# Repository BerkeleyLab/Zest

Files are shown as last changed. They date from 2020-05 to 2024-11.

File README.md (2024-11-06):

# Zest board

Zest (Z=e^(st)) is a double FMC mezzanine board performing Analog to Digital and Digital to Analog conversions.
This board is mainly used as a part of Radio Frequency (RF) controls electronics systems in particle accelerators.
Over 400 units have been manufactured by Berkeley Lab and SLAC National Laboratories and is the ADC/DAC board base design of the
LCLS-II (Linac Coherent Light Source II) Low-Level RF (LLRF) system at SLAC.

The schematic is in gschem format; to work with it you
need [gschem](http://wiki.geda-project.org/geda:gaf) installed.
Tested on [Debian](https://www.debian.org) Jessie, Stretch, or Buster, where
you simply `apt-get install geda-gschem`.

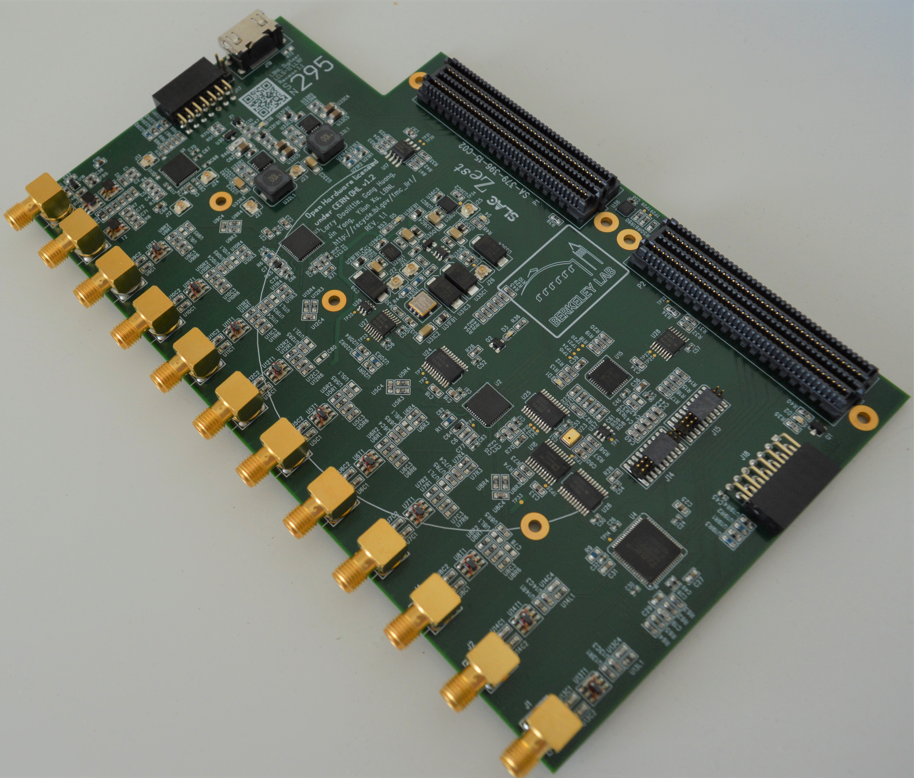
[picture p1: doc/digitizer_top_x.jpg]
Image of completed board
 

The Zest board features:

* 8 x transformer-coupled inputs sampled at 95 MS/s (2 x AD9653)
* 2 x transformer-coupled outputs sampled at 190 MS/s (AD9781)
* Input clock source up to 3 GHz (LMK01801, no on-board oscillator)
* Extra clock divider output
* 2 x Pmod digital I/O
* Interface to FPGA via dual-LPC-FMC connectors
* 181.8 x 110 mm, 8-layer, with notch to accommodate Xilinx FMC eval boards, also known to work with [Marble](https://github.com/BerkeleyLab/Marble) and [Marble-Mini](https://github.com/BerkeleyLab/Marble-Mini)
* 4W power dissipation

This design has been skillfully ported to [KiCad](https://www.kicad.org/) 8 by Gang Huang.
Go [here](https://gitlab.com/lbl-boards/zest) for that work, now labeled Zest v1.2.

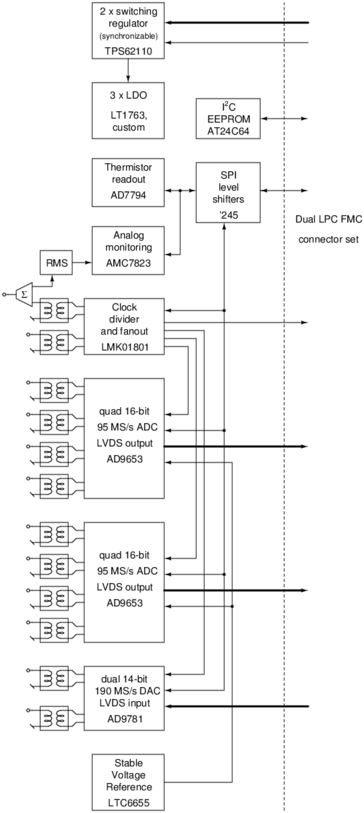
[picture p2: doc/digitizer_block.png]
block_diagram


## Schematics

To get PDF versions for reference:

  * Download the `djboxsym` tool. Put it in your PATH.

```bash
$ wget http://www.gedasymbols.org/user/dj_delorie/tools/djboxsym
$ echo "1a372fdef8e474119fae8acde38226f82271b62cd16b7f47b6b2408f0c0dd1ea  djboxsym" | sha256sum -c
djboxsym: OK
```

  * call `make` in `geda_library/symbol/djboxsym/`, which generates symbols from the included symbol templates
  * call `make` in `digitizer/`, which should generate `digitizer_schematic.pdf`

## Artwork/Gerbers

Created by Kathy Pham at SLAC using PADS.  The latest version is from May 19, 2017.
The PADS design imports the netlist exported from this gschem design.
These PADS pcb file is in the top directory in this repository (`PC-379-396-15-C02_DIGITIZER BOARD.pcb`) and the gerbers
are in the `gerbers` directory.

QR-code serial-number overlay Gerbers are generated with `qr_gen.py`.

## BOM

The BOM is also in the top directory in this repository (`PC-379-396-15-C02_DIGITIZER BOARD_XY.xlsx`).
This file was exported from the PADS design referenced above.

If you run `make merged_xy.csv`, you can merge the actual orderable part numbers (kept here
in the parts.data file) and get a usable xy assembly file for fabrication.

## Plastic Cover

One corner of the digitizer (by J3, clock input) has some fragile transformers
very close to where SMA wrenches are used.
It has proved helpful to have a protective cover in place to avoid damage.
This is designed in [OpenSCAD](http://www.openscad.org/) with a process that
matches up its features with the Gerber file; see covergen.py.
The OpenSCAD source file is cover1.scad.
OpenSCAD will export an STL file which is easily 3-D printed.

## References

 G. Huang, L. R. Doolittle, J. Yang, Y. Xu,
*"Low Noise Digitizer Design for LCLS-II LLRF,"* in NAPAC2016
[TUPOA40](https://accelconf.web.cern.ch/napac2016/papers/tupoa40.pdf).

## Copyright

Zest Copyright (c) 2019, The Regents of the University of California, through Lawrence Berkeley National Laboratory (subject to receipt of any required approvals from the U.S. Department of Energy), and The Board of Trustees of the Leland Stanford Junior University. All rights reserved.

This documentation describes Zest and is licensed under the CERN OHL v. 1.2.

NOTICE. This documentation was developed under funding from the U.S. Department of Energy and the U.S. Government consequently retains certain rights. As such, the U.S. Government has been granted for itself and others acting on its behalf a paid-up, nonexclusive, irrevocable, worldwide license in the documentation to reproduce, distribute copies to the public, prepare derivative works, and perform publicly and display publicly, and to permit others to do so.

You may redistribute and modify this documentation under the terms of the CERN OHL v.1.2. (http://ohwr.org/cernohl). THIS DOCUMENTATION IS PROVIDED BY THE COPYRIGHT HOLDERS AND CONTRIBUTORS "AS IS" AND ANY EXPRESS OR IMPLIED WARRANTIES, INCLUDING, BUT NOT LIMITED TO, THE IMPLIED WARRANTIES OF MERCHANTABILITY AND FITNESS FOR A PARTICULAR PURPOSE ARE DISCLAIMED. IN NO EVENT SHALL THE COPYRIGHT OWNER OR CONTRIBUTORS BE LIABLE FOR ANY DIRECT, INDIRECT, INCIDENTAL, SPECIAL, EXEMPLARY, OR CONSEQUENTIAL DAMAGES (INCLUDING, BUT NOT LIMITED TO, PROCUREMENT OF SUBSTITUTE GOODS OR SERVICES; LOSS OF USE, DATA, OR PROFITS; OR BUSINESS INTERRUPTION) HOWEVER CAUSED AND ON ANY THEORY OF LIABILITY, WHETHER IN CONTRACT, STRICT LIABILITY, OR TORT (INCLUDING NEGLIGENCE OR OTHERWISE) ARISING IN ANY WAY OUT OF THE USE OF THIS SOFTWARE, EVEN IF ADVISED OF THE POSSIBILITY OF SUCH DAMAGE. Please see the CERN OHL v.1.2 for applicable conditions.

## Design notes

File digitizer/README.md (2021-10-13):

# LCLS-II LLRF Digitizer Board

This directory holds the schematics and associated files (but not the layout)
for the LCLS-II LLRF Digitizer Board, currently Rev. 1.1.
It is in gschem format; to work with it you
need [gschem](http://wiki.geda-project.org/geda:gaf) installed.
Tested on [Debian](https://www.debian.org) Jessie or Stretch, where
you simply `apt-get install geda-gschem`.

Image of completed board [block diagram](../../doc/digitizer_block.png)

The digitizer board features:

* 8 x transformer-coupled inputs sampled at 95 MS/s (2 x AD9653)
* 2 x transformer-coupled outputs sampled at 190 MS/s (AD9781)
* Input clock source up to 3 GHz (LMK01801, no on-board oscillator)
* Extra clock divider output
* 2 x Pmod digital I/O
* Interface to FPGA via dual-LPC-FMC connectors
* 181.8 x 110 mm, with notch to accommodate Xilinx FMC eval boards
* 4W power dissipation

## Schematics

To get PDF versions for reference,
simply `make` in this directory.  The result is digitizer_schematics.pdf.

## Artwork/Gerbers

Created by Kathy Pham at SLAC using PADS.  Latest is 20170519.
The PADS design imports the netlist exported from this gschem design.
These PADS files are _not_ kept in this git repository, but
their SHA256 signatures are kept in the
[layout_20170519.sha256sum](layout_20170519.sha256sum) file in this directory.

QR-code serial-number overlay Gerbers are generated with `qr_gen.py`.

## BOM

Get a copy of the `PC-379-396-15-C02_DIGITIZER BOARD_XY.xlsx` file exported from
the PADS design reference above, and place it in this directory.

Then `make merged_xy.csv` to merge the actual orderable part numbers (kept here
in the parts.data file) and get a usable xy assembly file for fabrication.

## Plastic Cover

One corner of the digitizer (by J3, clock input) has some fragile transformers
very close to where SMA wrenches are used.
It has proved helpful to have a protective cover in place to avoid damage.
This is designed in [OpenSCAD](http://www.openscad.org/) with a process that
matches up its features with the Gerber file; see covergen.py.
The OpenSCAD source file is cover1.scad.
OpenSCAD will export an STL file which is easily 3-D printed.

## References

 G. Huang, L. R. Doolittle, J. Yang, Y. Xu,
*``Low Noise Digitizer Design for LCLS-II LLRF,''* in NAPAC2016
[TUPOA40](http://accelconf.web.cern.ch/AccelConf/napac2016/papers/tupoa40.pdf).

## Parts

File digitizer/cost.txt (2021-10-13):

As of 2015-08-21

Digi-Key BOM/shopping cart creation (based on orderable.txt) is
half-broken, but I can tell that qty. 25 parts cost is $743.42.

 2  ASP-134604-01   @newark          16.37
10  TCM4-19+        @minicircuits     2.09
 2  TCM2-43X+       @minicircuits     3.29
 1  TCP-2-33W+      @minicircuits     2.99

total non-Digi-Key: $63.21

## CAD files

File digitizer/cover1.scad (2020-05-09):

/* Digitizer cover to protect its transformers near J3 and J20 */
/* Obsolete, see cover2c.scad */
/* See also covergen.py */

/* 5 mm from board to attached SMA connector, which still fits in */
/* the 7.9 mm cutout for the board-mount SMA connector. */
/* 7 mm from board to the beginning of the hex section. */
/* Part is 5.5 mm thick, to avoid slight interference with SMA connectors found with a 6mm thick version. */

module cover()
{
  union() {
    difference() {
       union () {
          translate([0, -39.5, 2]) cube([40.5, 39.5, 3.5]);
          /* copper pad on board measures 5.8 mm dia */
          translate([37.55,-36.5, 0]) cylinder(r=2.9, h=4, $fn=30);
       }
       union () {
          /* 106.3 mil = 2.7 mm dia hole, tight clearance for 4-40 */
          translate([37.55, -36.5, -1]) cylinder(r=1.5, h=8, $fn=30);
          translate([ -1, -11.50, 0]) cube([10.6, 7.7, 8]);  /* J3  */
          translate([ -1, -26.75, 0]) cube([10.6, 7.7, 8]);  /* J20 */
          translate([ -1, -42.00, 0]) cube([10.6, 7.7, 8]);  /* J11 */
          /* TCM4-19 datasheet claims max height 4.06 mm, I measure 3.1 mm */
          translate([11.3, -15.2, 0]) cube([4.2, 4, 4.0]);  /* U34 */
          translate([17.3, -15.2, 0]) cube([4.2, 4, 4.0]);  /* T1 */
          translate([11.3, -26.0, 0]) cube([4.2, 4, 4.0]);  /* T1 */
          translate([39, -24, 1]) mirror(v=[1, 0, 0]) linear_extrude(height = 1.5) {
              text("LBNL", size = 6.2, font = "Liberation Sans");
          }
          translate([28, -34, 1]) mirror(v=[1, 0, 0]) linear_extrude(height = 1.5) {
              text("R3", size = 6.2, font = "Liberation Sans");
          }
       }
    }
    /* these are the stubs supposed to rest on the bare board */
    translate([0,    -3.6, 0]) cube([ 9.5, 3.6, 2]);
    translate([0,   -18.2, 0]) cube([ 9.5, 3.6, 2]);
    translate([0,   -33.1, 0]) cube([16.0, 5.2, 2]);
    translate([25.3, -6.1, 0]) cube([ 9.5, 6.1, 2]);
  }
}

cover();

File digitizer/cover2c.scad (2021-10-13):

/* Digitizer cover to protect its transformers near J3 and J20 */
/* See below for connection to covergen.py */

/* 5 mm from board to attached SMA connector, which still fits in */
/* the 7.9 mm cutout for the board-mount SMA connector. */
/* 7 mm from board to the beginning of the hex section. */
/* Part is 5.5 mm thick, to avoid slight interference with SMA connectors found with a 6mm thick version. */

module base_cube(x1, y1, dx, dy, h)
{
    translate([x1,  y1, 0]) cube([ dx, dy, h]);
}

/* Generated by covergen2.py */
include <cover2_layers.dat>

module cover()
{
  union() {
    difference() {
       union () {
          translate([0, -181.5, 2]) cube([40.5, 181.5, 3.5]);
          /* copper pad on board measures 5.8 mm dia */
          translate([37.55, -36.50, 0]) cylinder(r=2.9, h=4, $fn=30);
          translate([38.69, -77.90, 0]) cylinder(r=2.9, h=4, $fn=30);
          translate([32.47,-146.99, 0]) cylinder(r=2.9, h=4, $fn=30);
       }
       union () {
          /* 106.3 mil = 2.7 mm dia hole, tight clearance for 4-40 */
          translate([37.55, -36.50, -1]) cylinder(r=1.5, h=8, $fn=30);
          translate([38.69, -77.90, -1]) cylinder(r=1.5, h=8, $fn=30);
          translate([32.47,-146.99, -1]) cylinder(r=1.5, h=8, $fn=30);
          layer3();
          layer2();
          translate([39, -24, 1]) mirror(v=[1, 0, 0]) linear_extrude(height = 1.5) {
              text("LBNL", size = 6.2, font = "Liberation Sans");
          }
          translate([28, -34, 1]) mirror(v=[1, 0, 0]) linear_extrude(height = 1.5) {
              text("R4", size = 6.2, font = "Liberation Sans");
          }
       }
    }
    layer1();
  }
}

cover();

/* set up the initial view */
$vpr = [156, 0, 100];
$vpt = [56, -86, -71];
$vpd = 140;

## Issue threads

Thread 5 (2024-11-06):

### ISSUE TITLE
Paper link 404

### ISSUE THREAD

**Issue by mdavidsaver** [BerkeleyLab/Zest#5]
The CERN [link](http://accelconf.web.cern.ch/AccelConf/napac2016/papers/tupoa40.pdf) in the README now returns a 404.

https://github.com/BerkeleyLab/Zest/blob/43e8c67fba8082a3a21e5eda8ba646df3bf2c3b9/README.md?plain=1#L75C1-L77C80

**Comment by mdavidsaver** [comment]
I found what I think is a new URL.  Is this the same paper?

https://accelconf.web.cern.ch/napac2016/papers/tupoa40.pdf

**Comment by ldoolitt** [comment]
Yes.
`31e12ff99218b0af442ee49b99f9bdd18fad4b6ffb2036ee2ae2193ea4c42ac5  tupoa40.pdf`

**Comment by ldoolitt** [comment]
@mdavidsaver thanks for pointing this out!  Fixed.

**Comment by mdavidsaver** [comment]
You might want to add this citation to the README for the [gitlab](https://gitlab.com/lbl-boards/zest) project as well.

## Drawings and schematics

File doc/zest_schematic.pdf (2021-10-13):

# Clock distribution ADC

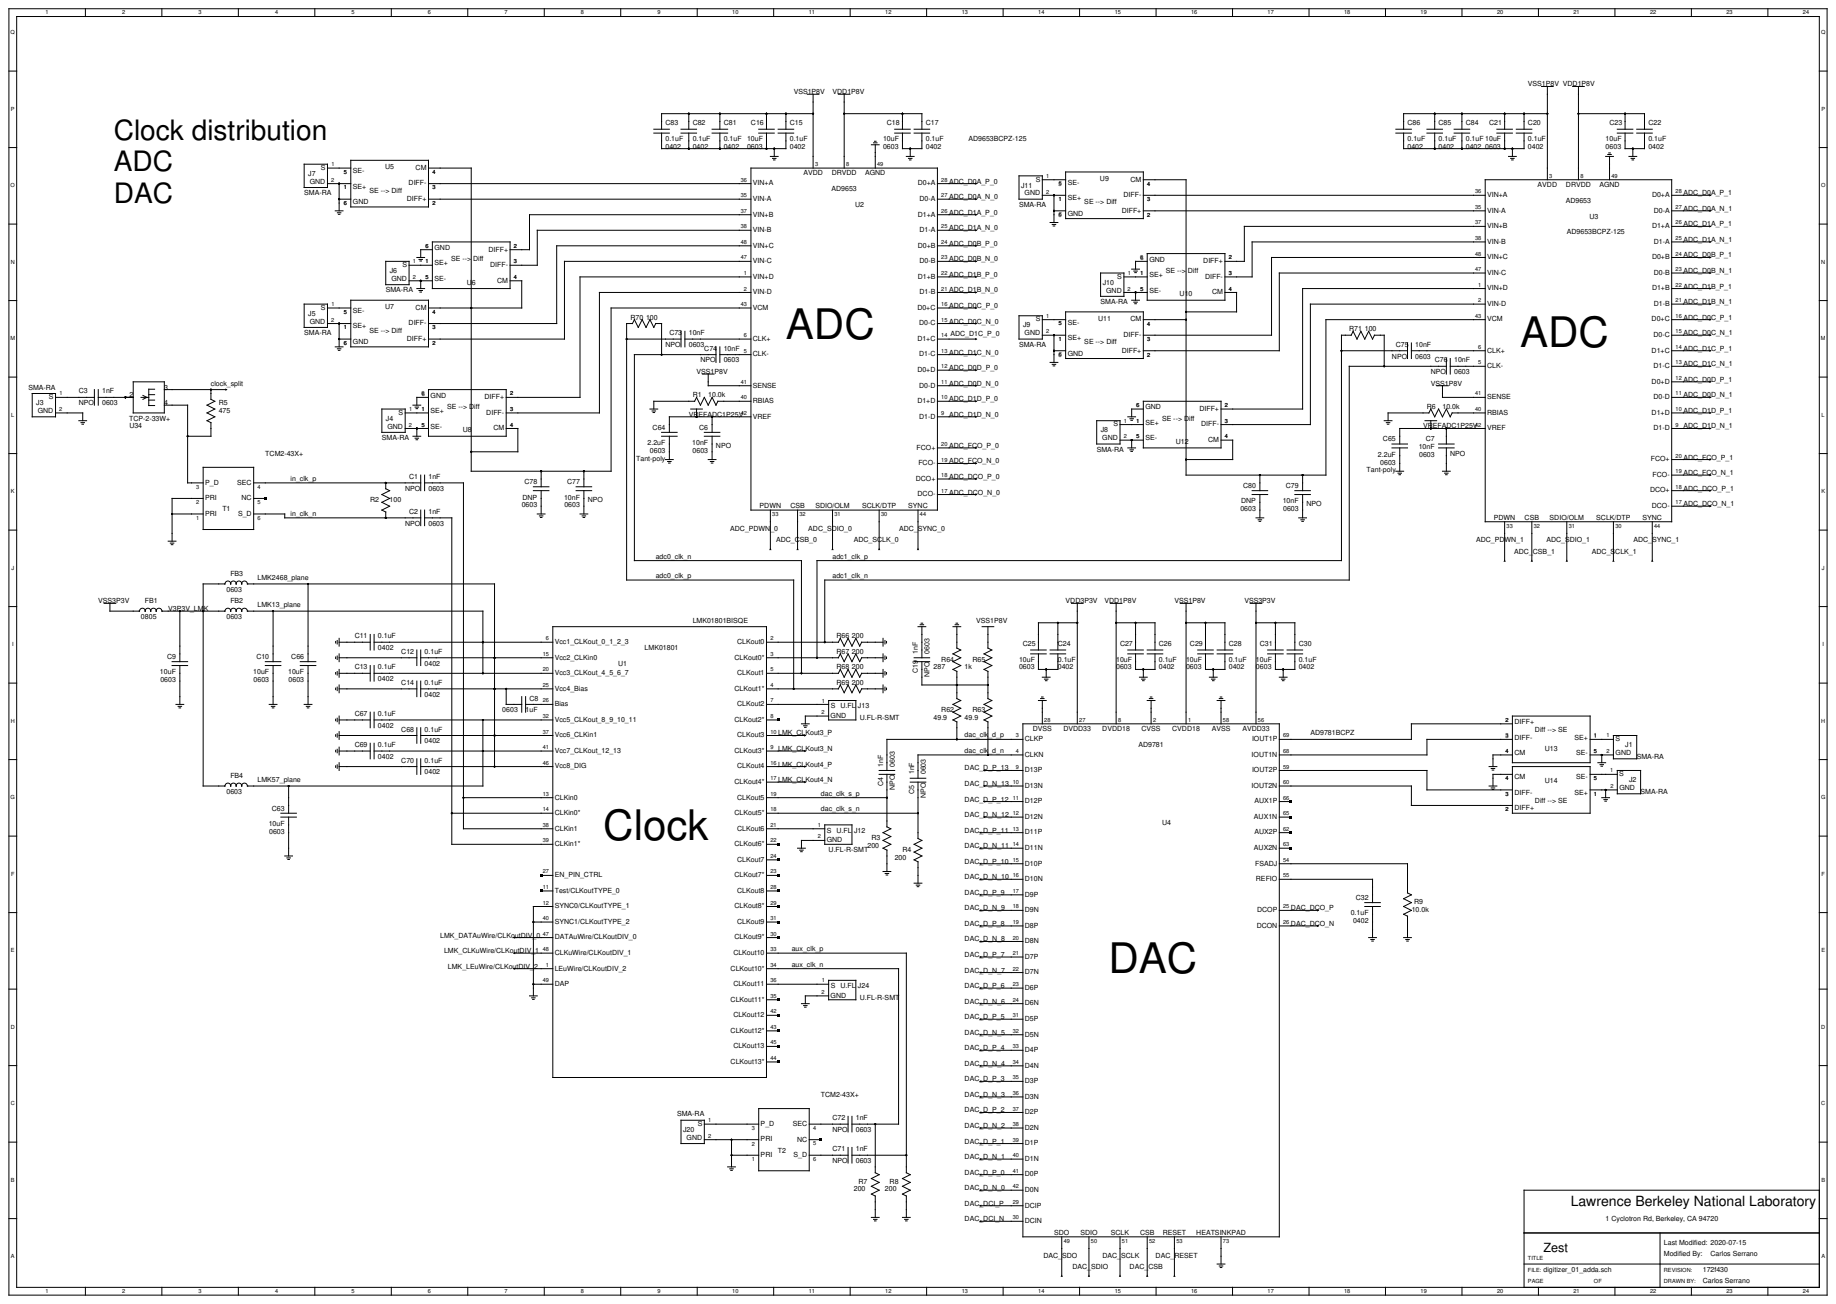
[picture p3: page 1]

Lawrence Berkeley National Laboratory

1 Cyclotron Rd, Berkeley, CA 94720

Zest | Last Modified: 2020-07-15 Modified By: Carlos Serrano

FILE: digitizer_01_adda.sch PAGE OF | REVISION: 172f430 DRAWN BY: Carlos Serrano

# LPC FMC P1

D1

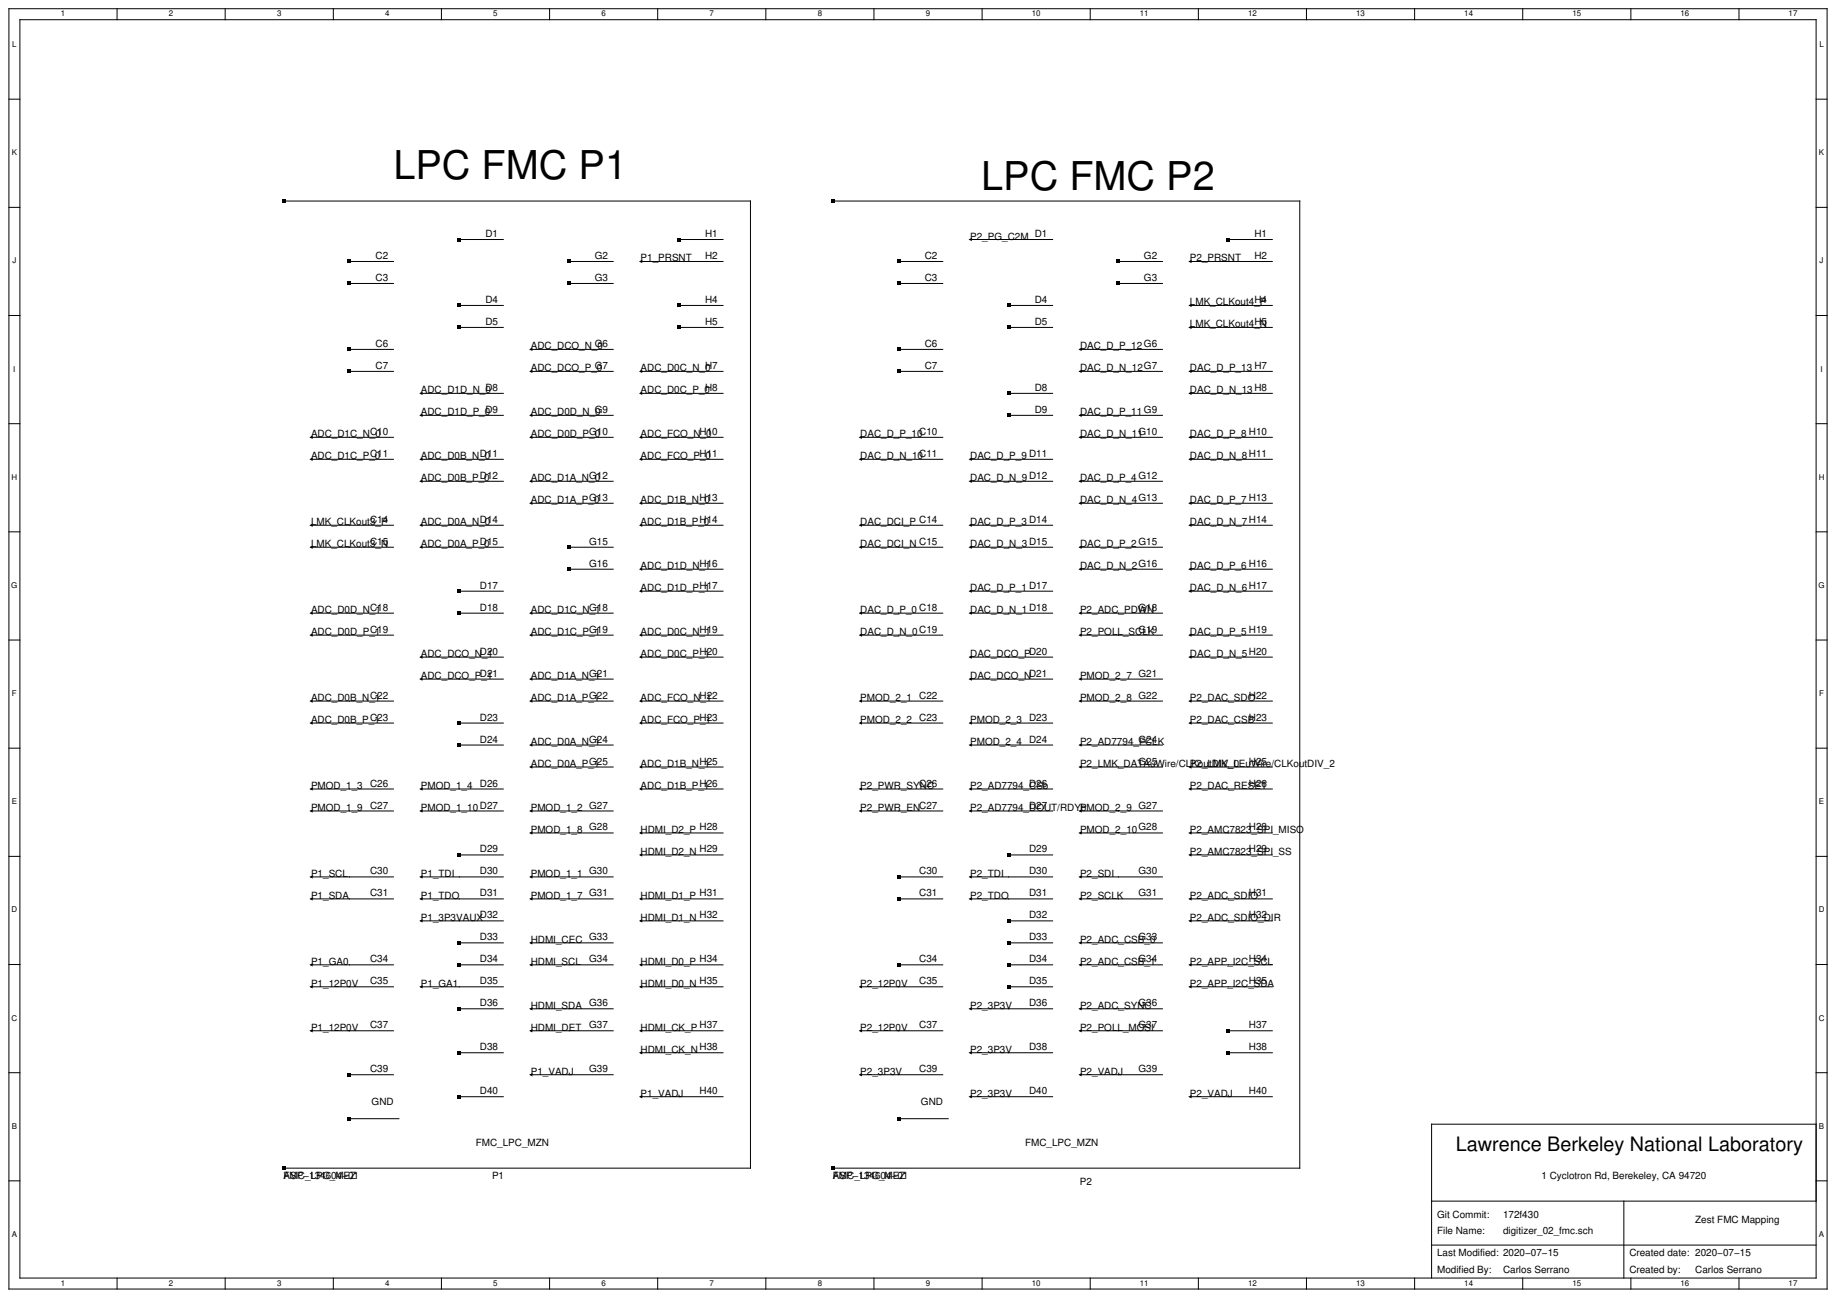
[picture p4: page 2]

Lawrence Berkeley National Laboratory

1 Cyclotron Rd, Berekeley, CA 94720

Git Commit: 172f430 File Name: digitizer_02_fmc.sch | Zest FMC Mapping

Last Modified: 2020−07−15 Modified By: Carlos Serrano | Created date: 2020−07−15 Created by: Carlos Serrano

# Housekeeping

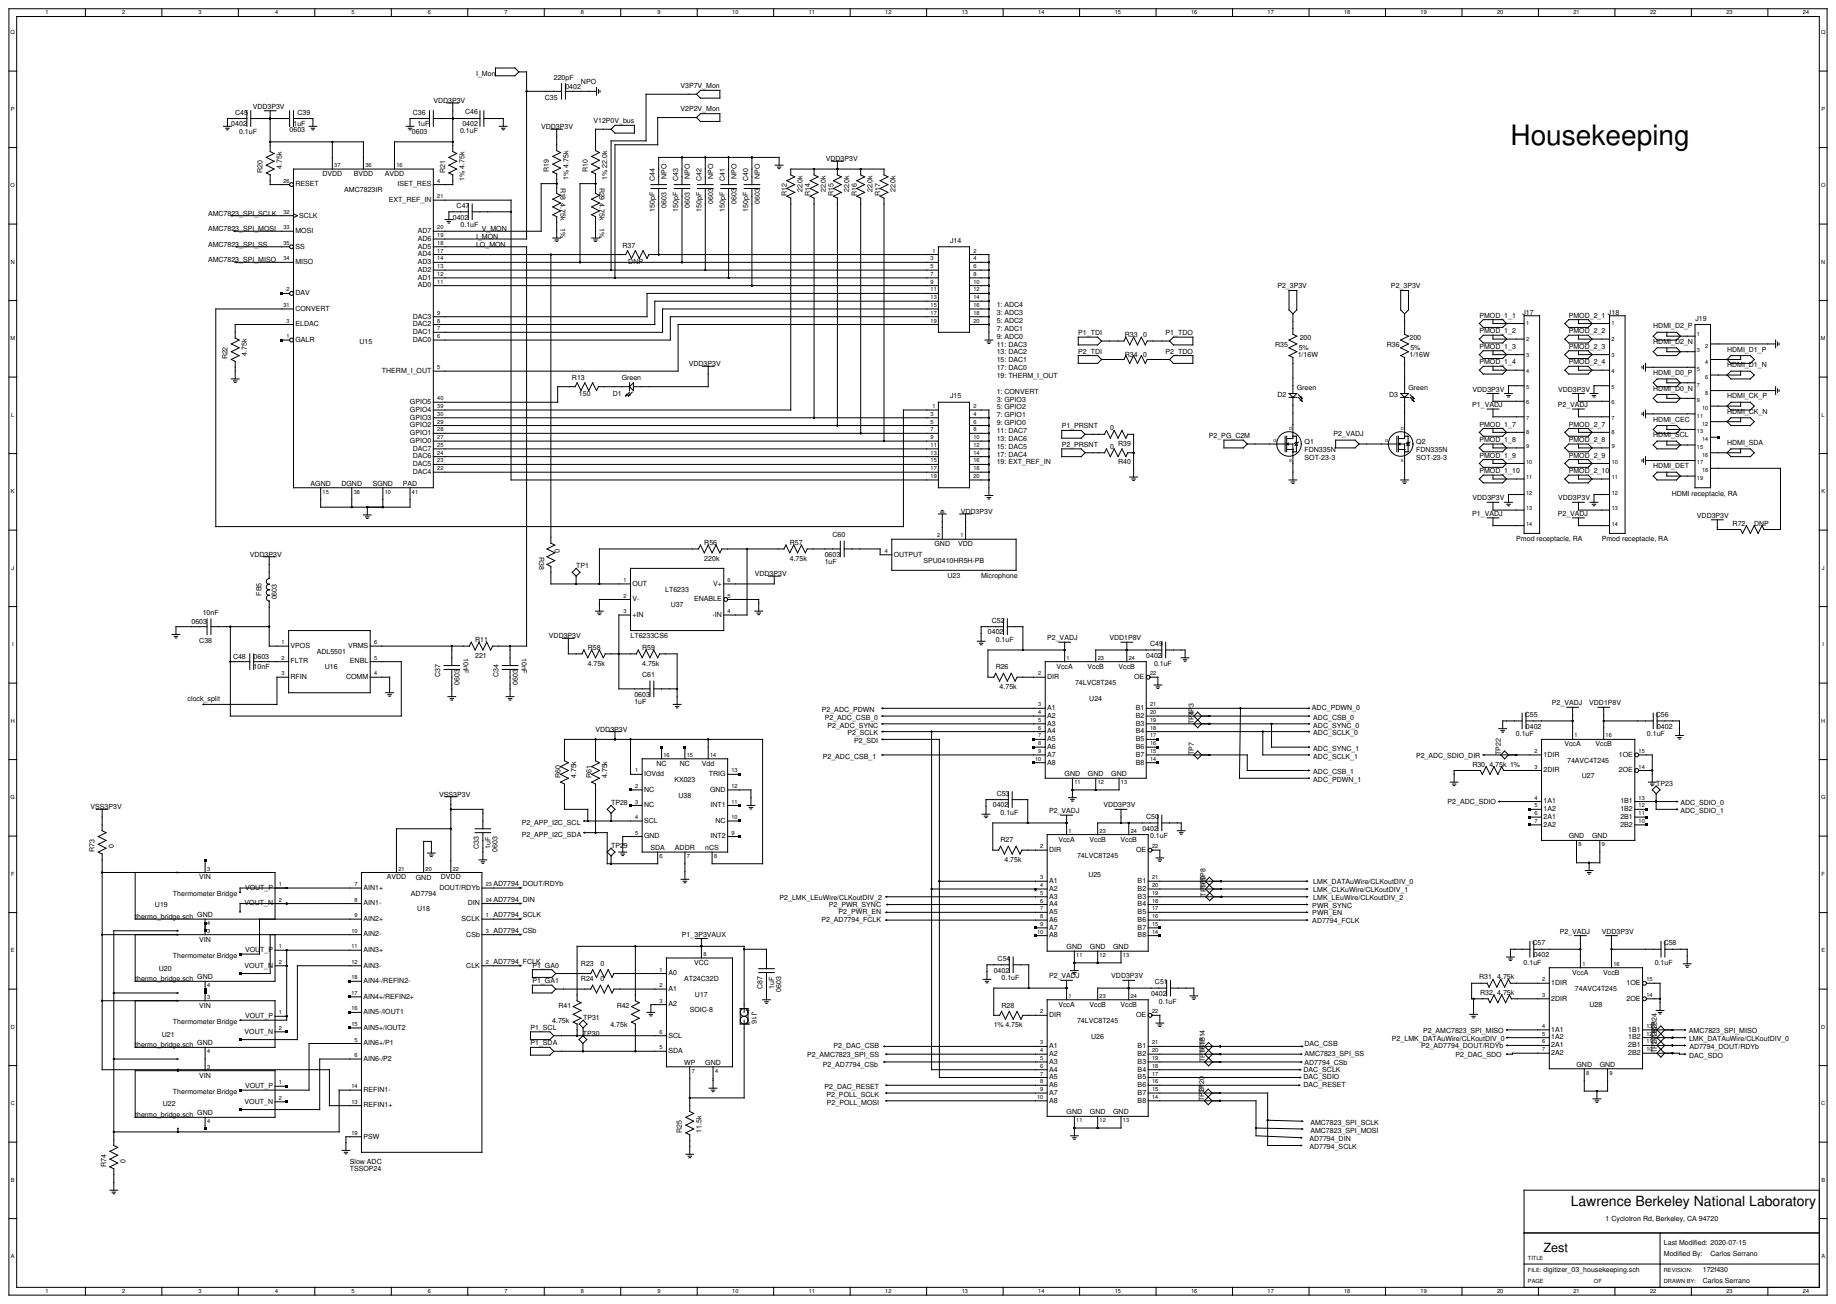
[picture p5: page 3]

9 | 10

13 | 14
15 | 16

Lawrence Berkeley National Laboratory

1 Cyclotron Rd, Berkeley, CA 94720

Zest | Last Modified: 2020-07-15 Modified By: Carlos Serrano

FILE: digitizer_03_housekeeping.sch PAGE OF | REVISION: 172f430 DRAWN BY: Carlos Serrano

D4

R48 | Green

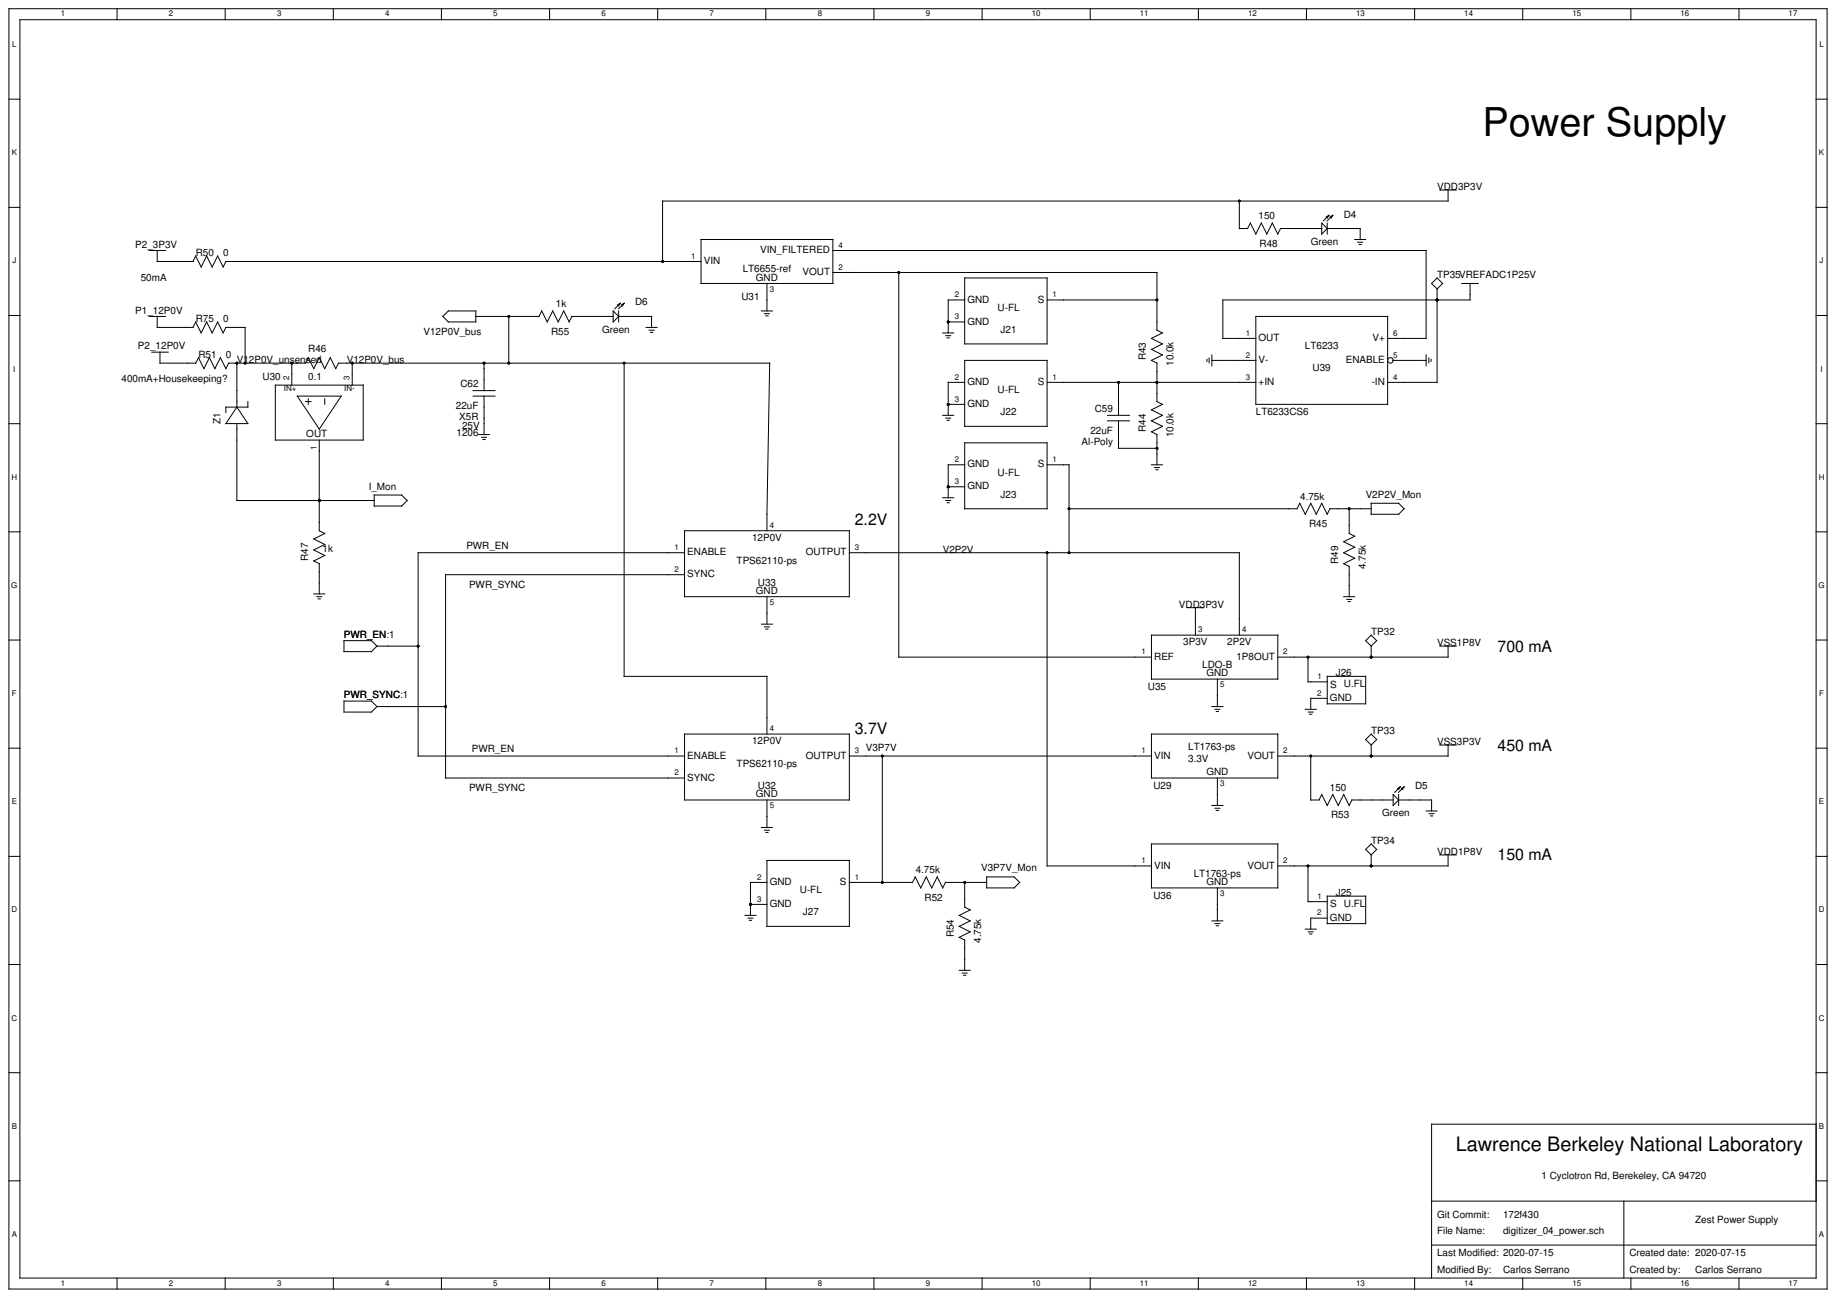
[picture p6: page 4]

SYNC ² | | D5 R53 Green

Lawrence Berkeley National Laboratory

1 Cyclotron Rd, Berekeley, CA 94720

Git Commit: 172f430 File Name: digitizer_04_power.sch | Zest Power Supply

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

F

F

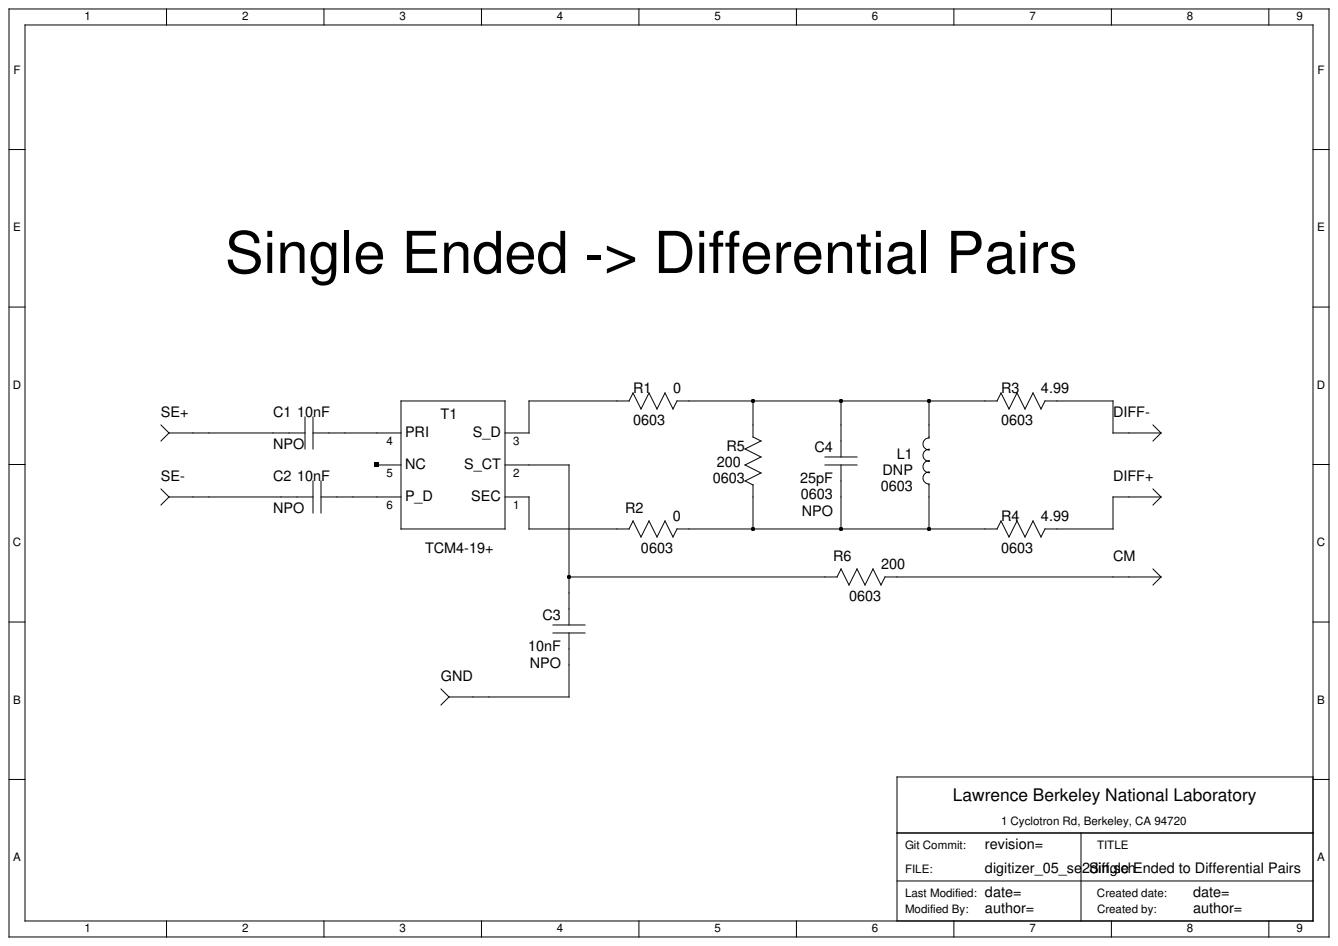
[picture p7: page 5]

Single Ended -> Differential Pairs

Lawrence Berkeley National Laboratory

1 Cyclotron Rd, Berkeley, CA 94720

revision= Git Commit: FILE: digitizer_05_se2diff.sch | TITLE Single Ended to Differential Pairs

date= Last Modified: Modified By: author= | date= Created date: Created by: author=

# Differential Pairs -> Single Ended

F

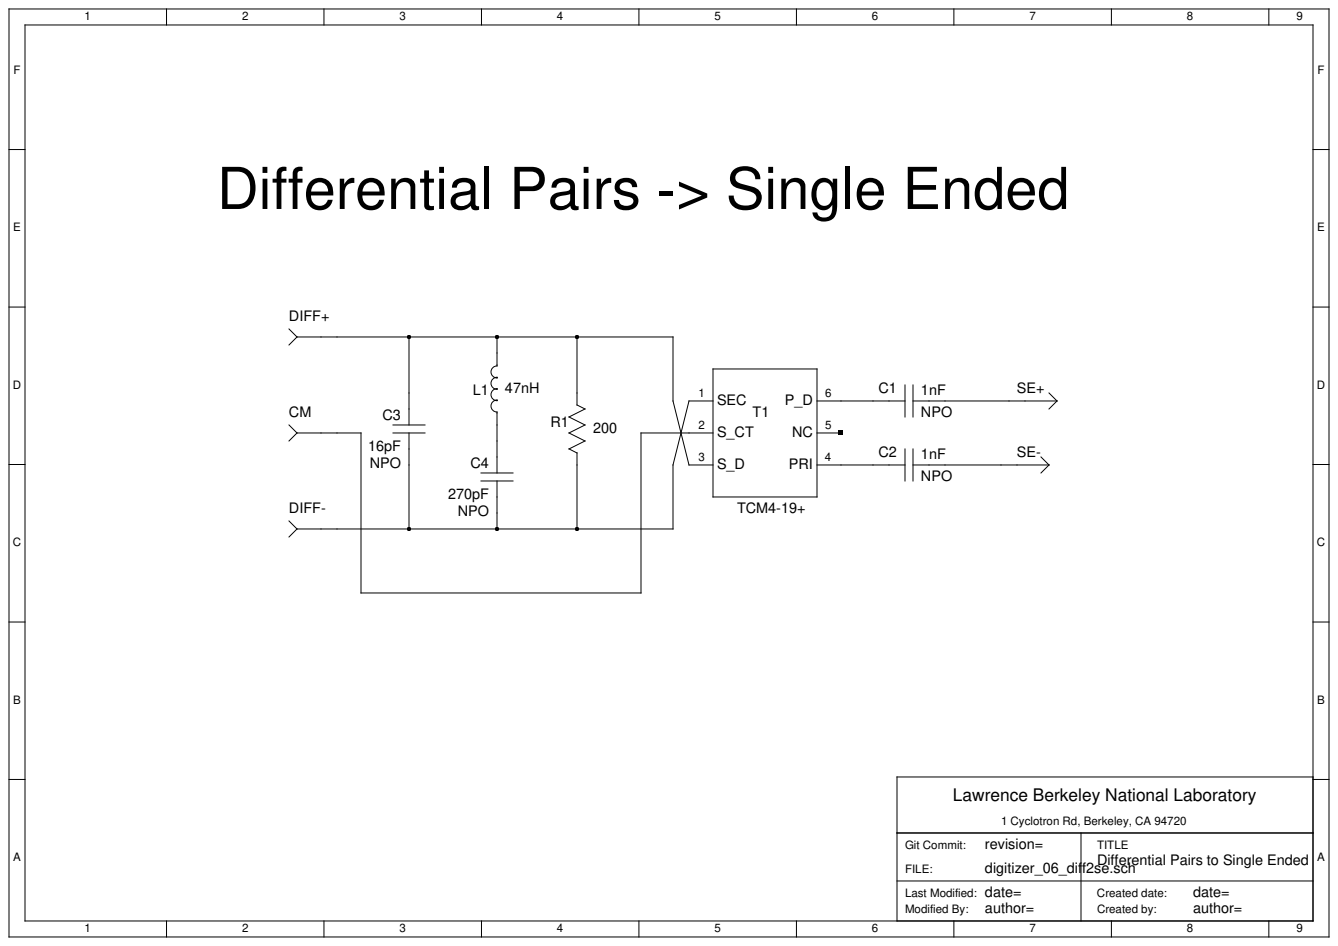
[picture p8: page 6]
NPO; SEC ¹; PRI; TCM4-19+; 16pF NPO; 270pF NPO; DIFF+ CM; DIFF-

Lawrence Berkeley National Laboratory

1 Cyclotron Rd, Berkeley, CA 94720

revision= FILE: Git Commit: digitizer_06_diff2se.sch | TITLE Differential Pairs to Single Ended

date= Last Modified: Modified By: author= | date= Created date: Created by: author=

D

E

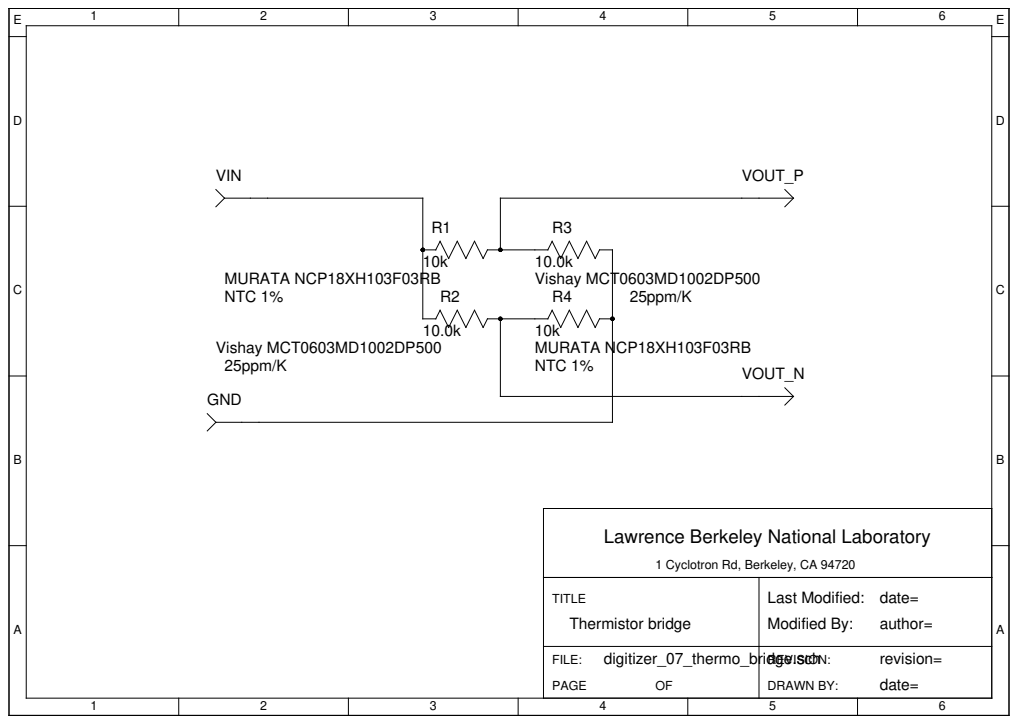
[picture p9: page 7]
10kΩ MURATA NCP18XH103F03RB; NTC 1%; 10.0kΩ Vishay MCT0603MD1002DP500 25ppm/K; 10.0kΩ Vishay MCT0603MD1002DP500; 25ppm/K; 10kΩ MURATA NCP18XH103F03RB NTC 1%; VIN; GND; VOUT_P; VOUT_N

Lawrence Berkeley National Laboratory

1 Cyclotron Rd, Berkeley, CA 94720

TITLE Thermistor bridge | Last Modified: date= Modified By: author=

FILE: digitizer_07_thermo_bridge.sch PAGE OF | REVISION: revision= DRAWN BY: date=

# LDO

F

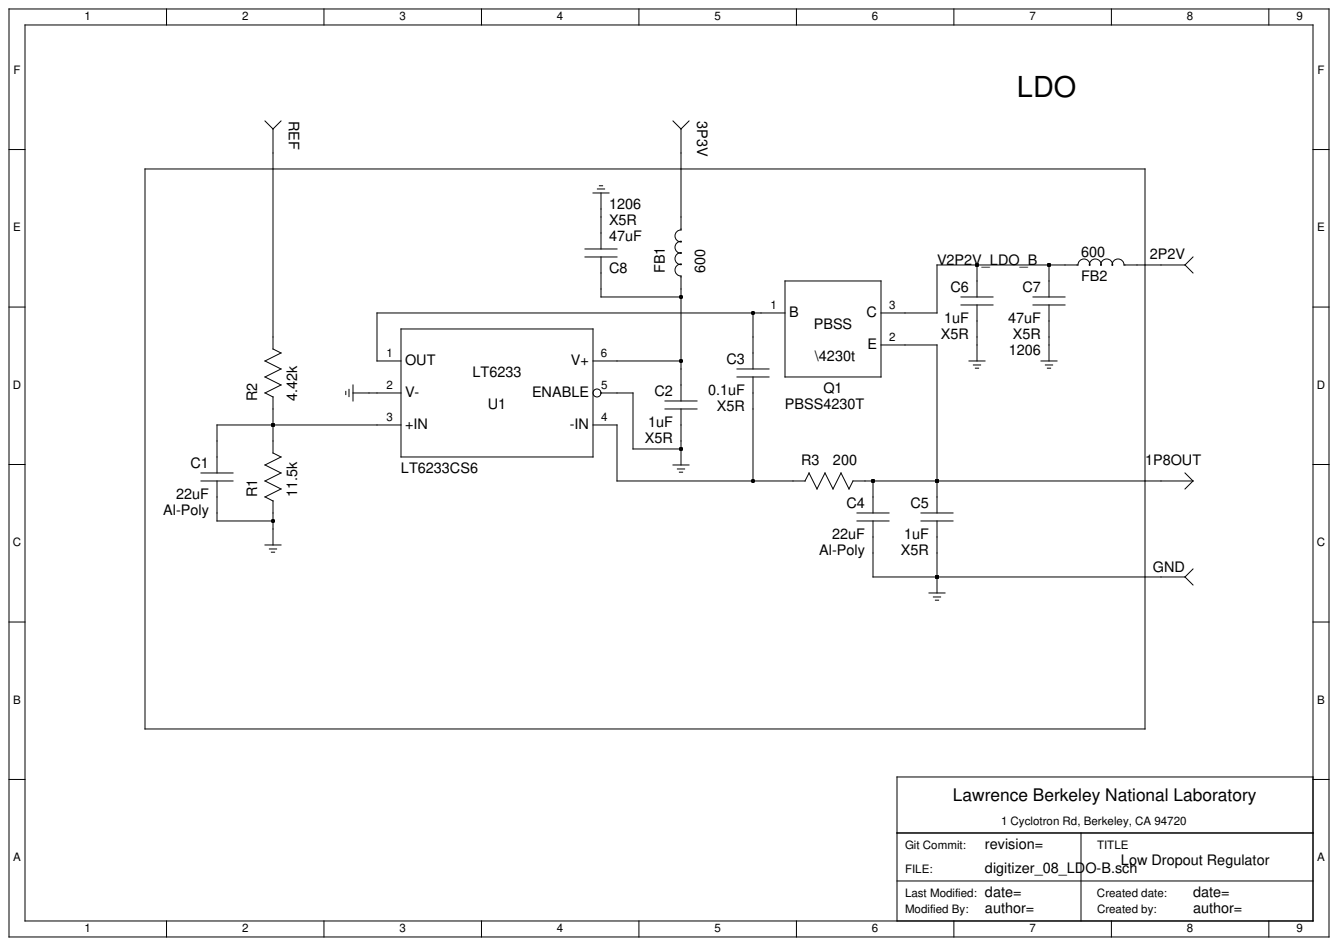
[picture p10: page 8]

Lawrence Berkeley National Laboratory

1 Cyclotron Rd, Berkeley, CA 94720

revision= Git Commit: FILE: digitizer_08_LDO-B.sch | TITLE Low Dropout Regulator

date= Last Modified: Modified By: author= | date= Created date: Created by: author=

# LT6655 2.5V Reference

# VIN

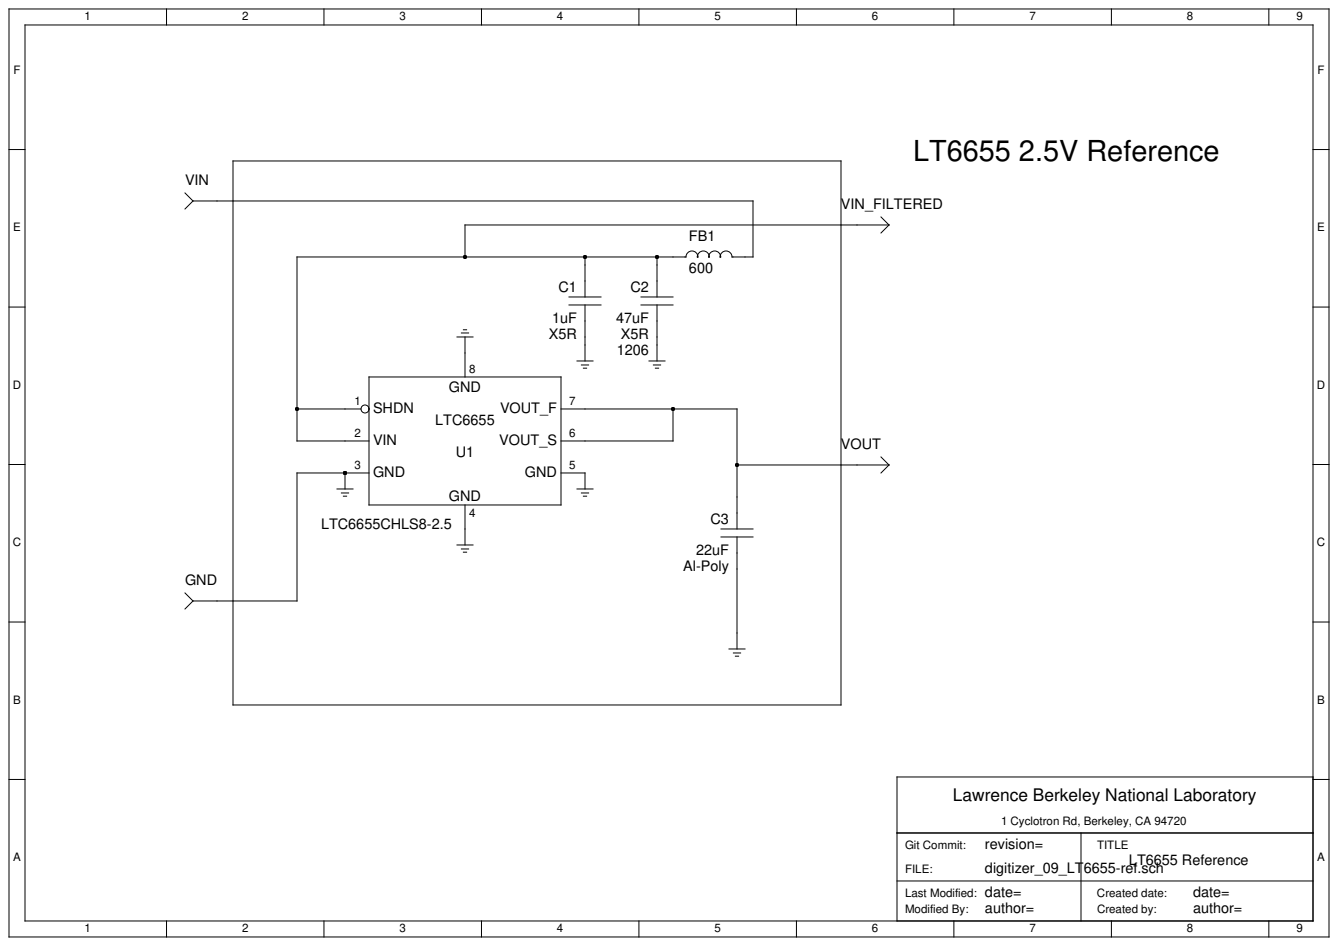
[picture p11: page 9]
22uF Al-Poly; LTC6655; SHDN ¹; VIN ²; GND ³; GND; VOUT_S; VOUT_F; LTC6655CHLS8-2.5; VOUT; VIN_FILTERED

Lawrence Berkeley National Laboratory

1 Cyclotron Rd, Berkeley, CA 94720

revision= Git Commit: FILE: digitizer_09_LT6655-ref.sch | TITLE LT6655 Reference

date= Last Modified: Modified By: author= | date= Created date: Created by: author=

# Switch Regulator

F

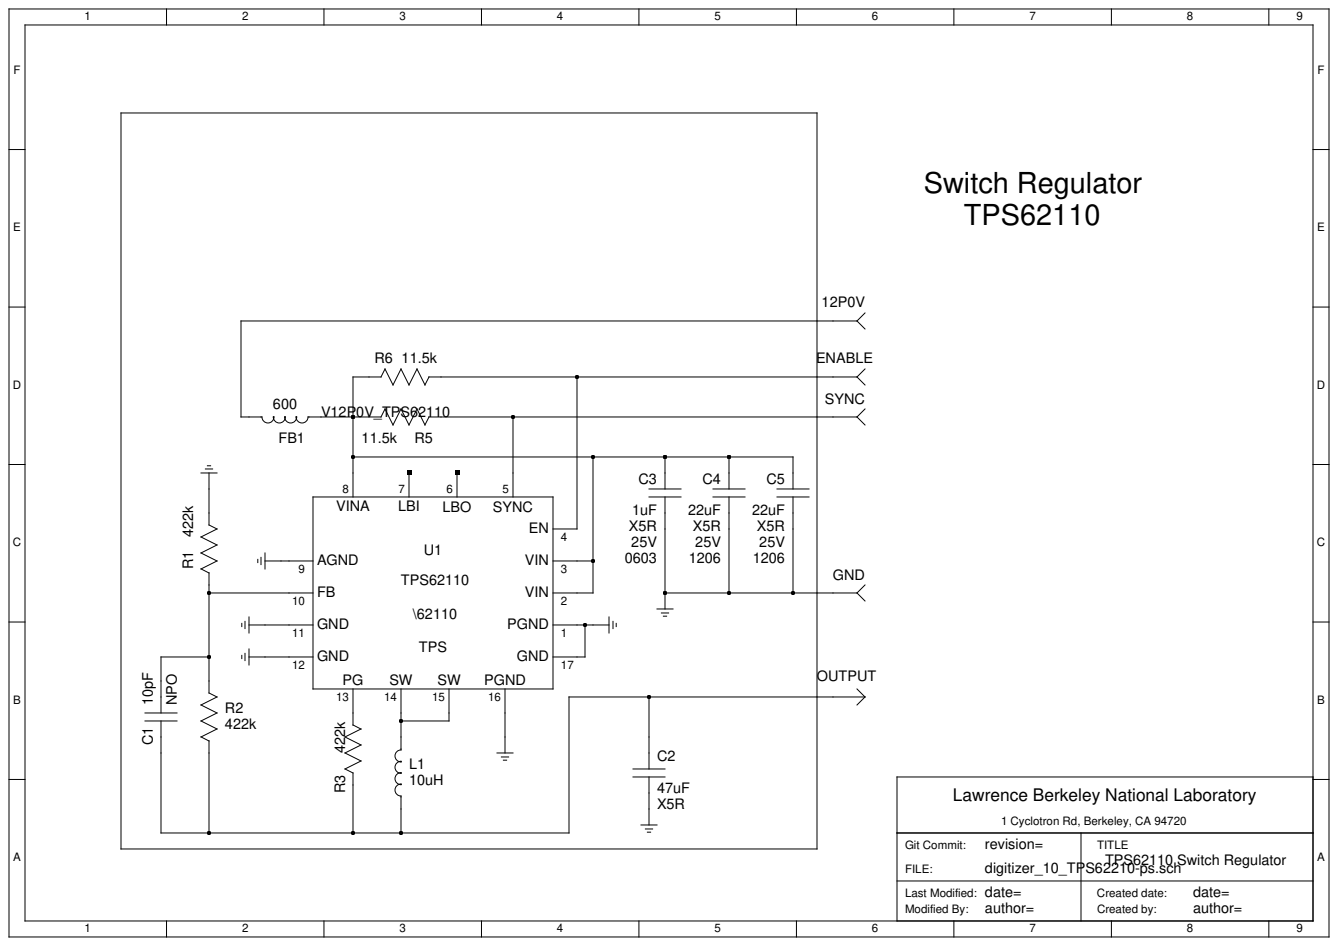
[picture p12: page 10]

Lawrence Berkeley National Laboratory

1 Cyclotron Rd, Berkeley, CA 94720

revision= Git Commit: FILE: digitizer_10_TPS62210-ps.sch | TITLE TPS62110 Switch Regulator

date= Last Modified: Modified By: author= | date= Created date: Created by: author=

F

F

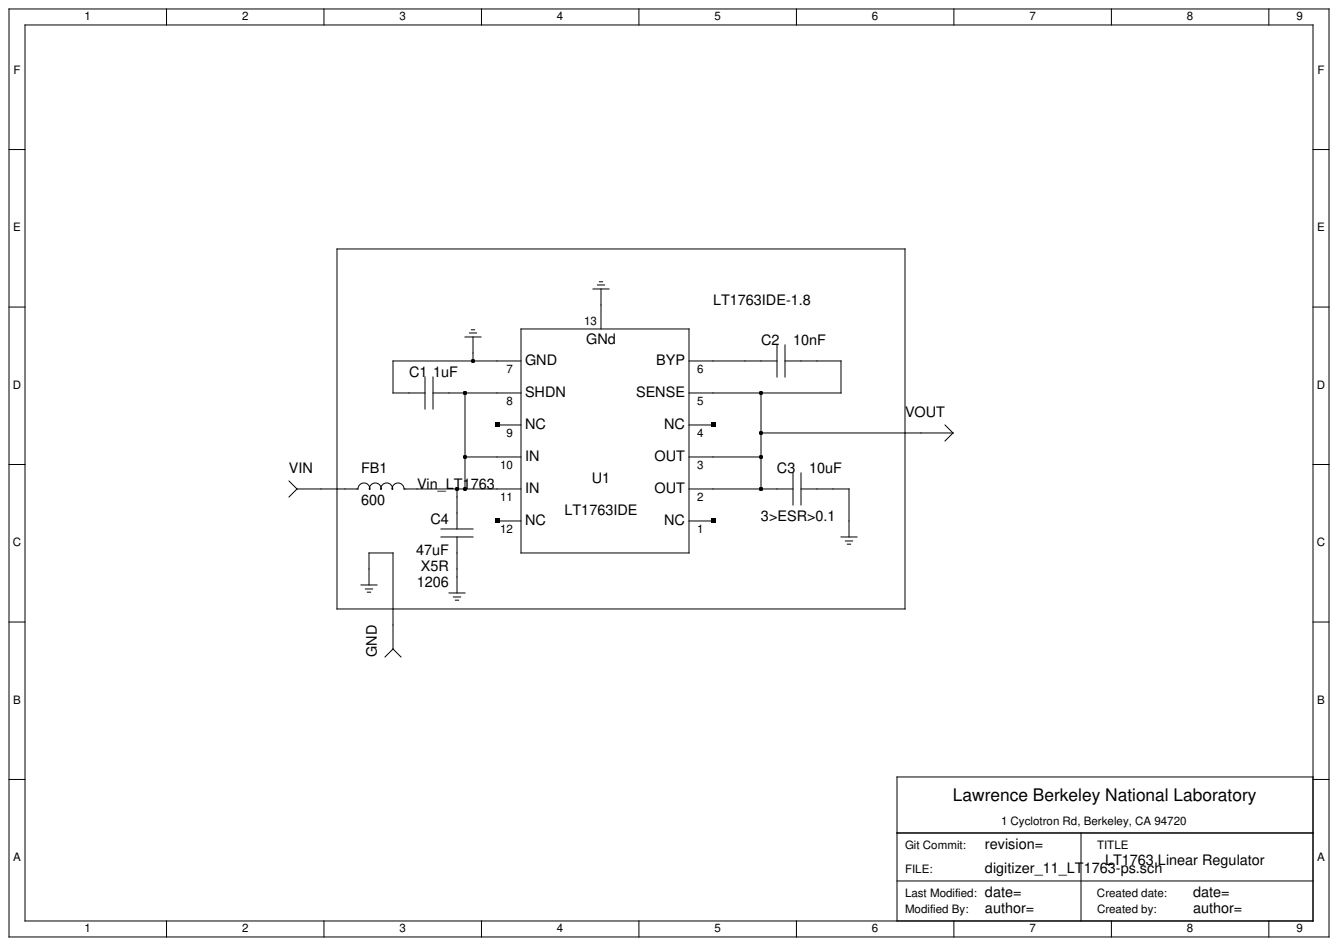
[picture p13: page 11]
LT1763IDE; OUT; SENSE; BYP 6 GND 7; SHDN 8; GNd; LT1763IDE-1.8; 3>ESR>0.1; GND; VOUT; VIN; Vin_LT1763

Lawrence Berkeley National Laboratory

1 Cyclotron Rd, Berkeley, CA 94720

revision= Git Commit: FILE: digitizer_11_LT1763-ps.sch | TITLE LT1763 Linear Regulator

date= Last Modified: Modified By: author= | date= Created date: Created by: author=

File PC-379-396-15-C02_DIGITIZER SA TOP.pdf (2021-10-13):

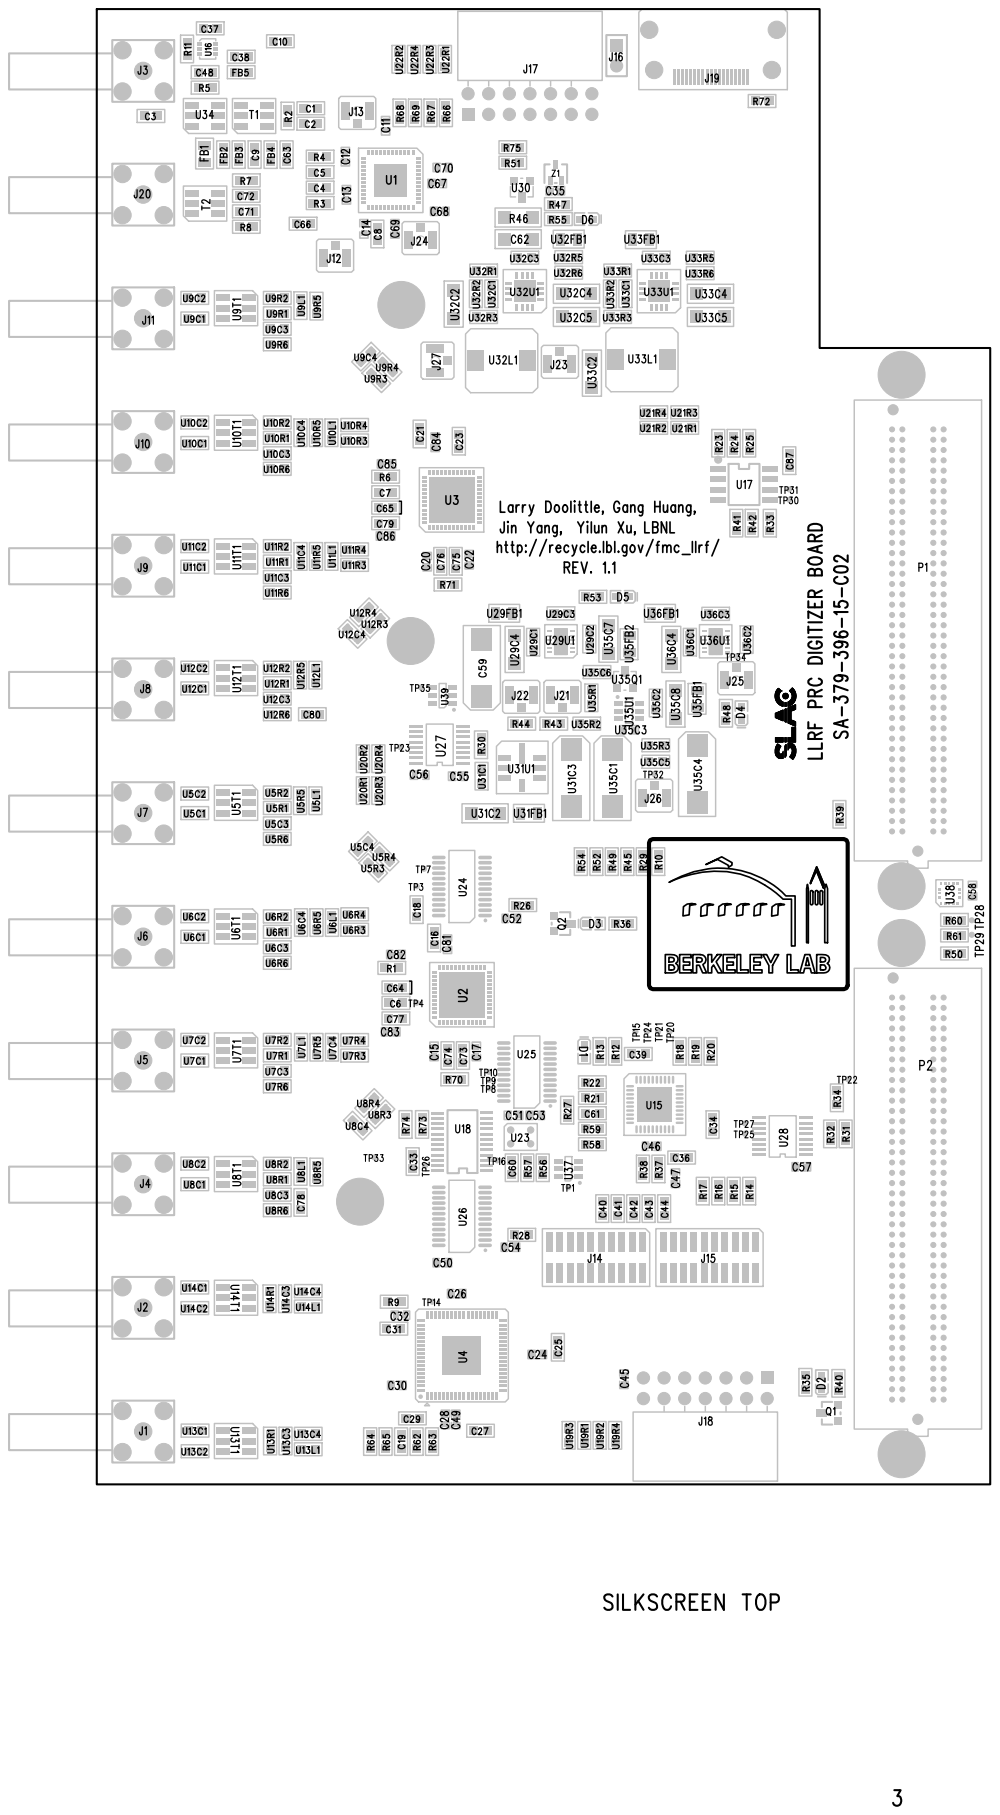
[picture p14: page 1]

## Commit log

2020-05-09 Put in some meaningful files
    Mostly documentation, still not the actual schematics
    [cover1.scad]
2020-07-16 Add digitizer directory as is from LBNL gitlab repository
    [cover1.scad, cover2c.scad, digitizer_01_adda.sch, digitizer_02_fmc.sch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]
2020-07-16 Added geda_library as is from LBNL repo, not as a submodule
    [LDO-B.sch, LT1763-ps.sch, LT6655-ref.sch, TPS62110-ps.sch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]
2021-10-13 Added gerbers, PADS file and others from SLAC
    [PC-379-396-15-C02_DIGITIZER BOARD_XY.xlsx, drl001.drl]
